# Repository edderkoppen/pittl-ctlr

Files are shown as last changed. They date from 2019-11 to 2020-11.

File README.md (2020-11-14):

# pittl-ctlr
Raspberry Pi TTL Controller, 0.2.0  
nGelwan | 2019

## Introduction
PiTTL is a collection of schematics and code which can be used to cheaply build a remotely-controllable random TTL sequence generator using a Raspberry Pi 4 (https://www.raspberrypi.org/products/raspberry-pi-4-model-b/) and a couple of additional hardware components. It consists of two parts, the PiTTL controller, contained in this repository, and the PiTTL client (https://github.com/extradosages/pittl-client). When pushed to the extreme, PiTTL supports generating sequences which run for at least a month consisting of pulses of less than 10ms duration. 

## Installation
### HAT Construction
If you don't have an already constructed PiTTL, one can be constructed relatively cheaply. The hardware for PiTTL has been designed like a Raspberry Pi HAT (https://www.raspberrypi.org/blog/introducing-raspberry-pi-hats/), to live on an auxiliary baord which talks to the Raspberry Pi via its GPIO headers. The schematics for the HAT are detailed in the **board** sub-repo (https://github.com/extradosages/pittl-ctlr/board), and can be viewed with EDA software. I used Eagle (https://www.autodesk.com/products/eagle/overview). The gerber files packaged in the **board** sub-repo can be supplied to a custom PCB-vendor in order to custom print the PCB for the HAT.

### Software Installation
One may install the PiTTL controller software on any Raspberry Pi, although the software has only been tested with the Raspberry Pi 4, and the practical limitation of the TTL driver listed above are given in the context of the hardware on a Raspberry Pi 4. Presumably, the software will function on a variety of operating systems, but certain features have been designed with Raspbian in mind (e.g. automatic start using systemd).

The only software prerequisites for the installation of pittld are python >=3.4, python setuptools, and a C-compiler for the compilation of pigpio. To setup and install the software, a very rudimentary shell script *setup/setup.sh* is provided, which should be run as root. Be warned, the setup script is non-transactional and doesn't try very hard to catch errors, so one should pay attention closely to stdout during the installation. If setup completes successfully, pittld may be started by entering

>*pittld*

at the command-line or-- assuming the installation of the systemd units succeeded-- automatically upon restart of the Raspberry Pi. The logs for pittld can be followed with  

>*journalctl -f -u pittld*

on Raspbian. Confirmation that pittld is running successfully can be found in journalctl or by observing updates on the HAT's LCD.

## Overview
### Usage
PiTTL can be used to stage and then generate individual sequences of TTL pulses, called **programs**. Generating-- also known as **staging**-- a program is a two-step process: first, the **timing** of the program is staged, and then the program's **sequence** is staged. If a sequence has been successfully staged, a program can be **started** and **stopped** at will.

**Timing** is specified with 3 parameters: the **total time**, **exposure fraction**, and **resolution**. Total time is the desired length of the program, exposure fraction is the desired fraction of the program during which TTL-on logic will occur, and resolution is the minimum width of a TTL-on pulse. The resolution parameter is *very* important. It drastically simplifies the algorithm for generating random sequences of pulses satisfying the desired exposure fraction. It is important to note that when these three parameters are supplied to PiTTL, that total time and exposure fraction will be adjusted so that the time spent in TTL-on and TTL-off are both integer multiples of the resolution, and so that they are as close to the values specified as possible. Thus, after staging, timing is converted into the **specified**, **adjusted**, and **digital** domains. The specified timing consists of those floating point values requested, adjusted are those values after adjustment for resolution, and digital are those values in integral units of resolution.

A **sequence** is literally a binary sequence representing the TTL-logic time-series of the program. PiTTL can be induced to randomly generate a sequence based on any valid staged timing. If a sequence has been staged and new timing is then staged, the two are then unrelated, and the staged sequence is purged.

Once a program has been **started**, the timing and the sequence are considered **committed**. New sequences and timing can be staged without interrupting the running program.

PiTTL is capable of evaluating the **progress** and **ETA** of a currently running program, and also **stopping** a program, clearing any committed timings and sequences.

This functionality is implemented via PiTTL controller's python API and publicly via the combination of the PiTTL controller's manager service and the PiTTL client (https://github.com/extradosages/pittl-client).

### Details
The PiTTL controller is organised into several related hardware components and software services. These are the:
1. Manager
2. TTL Driver
3. LCD
4. Connectivity monitor

The software services are packaged under the name **pittld**, for PiTTL Daemon.
#### The Manager
The manager provides a public endpoint for communicating with a PiTTL controller. It is the means by which a PiTTL client can command a PiTTL controller to stage timing and sequences and to start and stop programs, and also the means by which a PiTTL client can query a PiTTL controller for any staged or committed timing or sequences, or the progress of any running program.
#### The TTL Driver
This software service leverages the use of the python library PiGPIO (http://abyz.me.uk/rpi/pigpio/) and a MOSFET to generate the ~4.4V square wave pulses consituting a TTL pulse train.

This software includes the routines to approximately sample from the collection of all subsets of the unit interval with fixed measure without measure-zero components. A resolution parameter (defining the minimum width of a sampled pulse) specifies the accuracy (and memory burden) of the sampling routine, with asymptotic convergence to the ideal sampler upon decreasing the parameter. Once sampled, such a subset defines a pulse train via a mapping of the unit interval onto some interval (probably larger) interval of the time axis. Non-exhaustive testing has determined that *time \* resolution* reaches a practical minimum at ~10^-3 s^2 due to GPIO consdierations and that *time / resolution* reaches a practical maximum at ~0.2 \* 10\^9 due to memory considerations.

This software also contains routines to generate TTL-pulse trains of (ideally) arbitrary frequencey and duty-cycle, but as of 0.2.0 these have not been extensively tested.
#### The LCD
The PiTTL HAT was designed with a HD44780 16colx2row LCD which can convey information about connectivity and program progress without having to use the python API, pittld logs, or PiTTL client.
#### The Connectivity Monitor
The connectivity monitor supplies pittld with information regarding internet connectivity.

## Troubleshooting
If the PiTTL controller is not behaving as expected (usually indicated by oddities displayed on the HAT's LCD), or has encountered an error, the most robust way to fix the problem is to cycle the power on the Raspberry Pi. There has not yet been implemented a robust software means of resetting the pittld service.

Failure of the LCD on the PiTTL HAT should not a be a surprise. The HD44780 is cheap.

It is recommended that the PiTTL controller be installed on a dedicated Raspberry Pi, with a fresh OS. However, if it not the case, it is worth noting that
1. The PiTTL manager service needs to be able to listen on port 5000 in order to receive communications from a PiTTL client.

If problems persist, the software repository should be updated and the service reinstalled. If further problems persist, a fresh Raspbian should be installed.

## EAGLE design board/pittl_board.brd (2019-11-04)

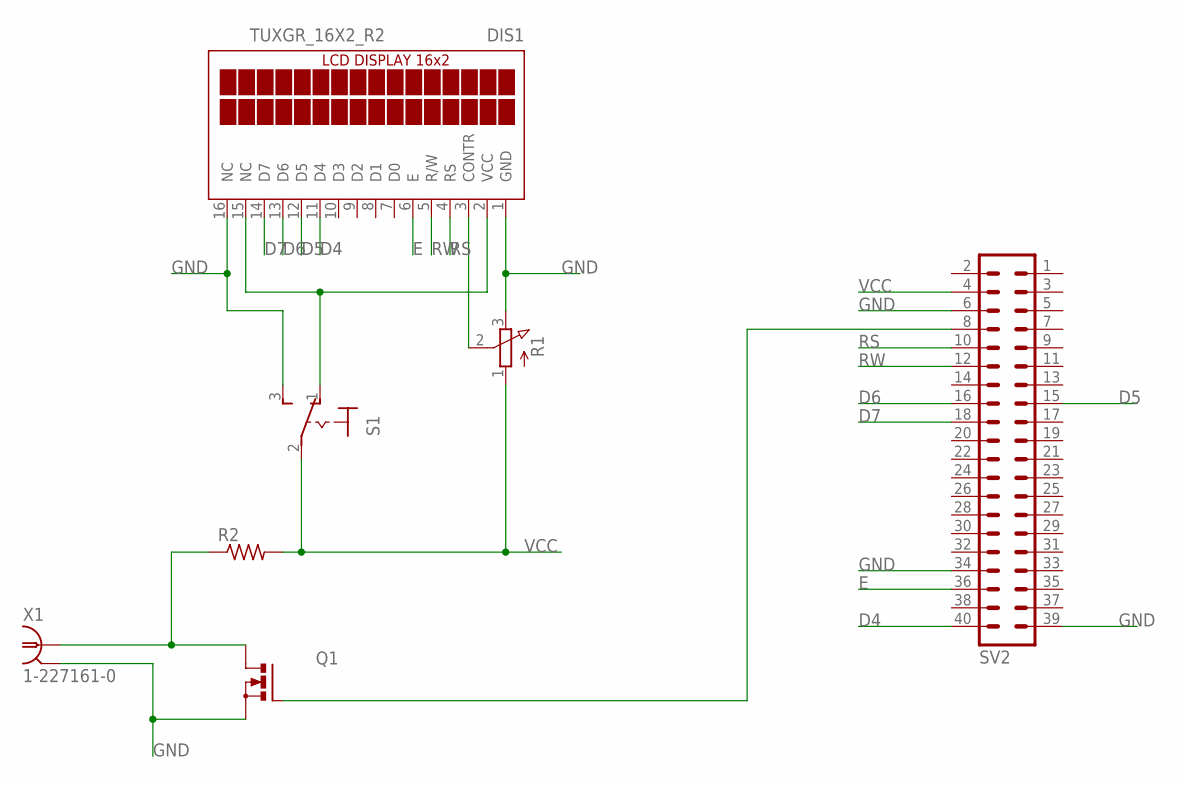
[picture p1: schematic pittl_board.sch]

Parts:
DIS1: TUXGR_16X2_R2
Q1: PMOSFET_NTO220BV; TO220BV
R1: 3RP/1610N
R2: R-US_0207/7; 0207/7
S1: 320-916
SV2: MA20-2W
X1: 1-227161-0; AMP_227161

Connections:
D4: DIS1.11 (D4), SV2.40
D5: DIS1.12 (D5), SV2.15
D6: DIS1.13 (D6), SV2.16
D7: DIS1.14 (D7), SV2.18
E: DIS1.6 (E), SV2.36
GND: DIS1.1 (GND), DIS1.16 (NC), Q1.S, R1.3 (E), S1.3 (S), SV2.6, SV2.34, SV2.39, X1.2
unnamed: Q1.G, SV2.8
unnamed: DIS1.2 (VCC), DIS1.15 (NC), S1.1 (O)
unnamed: DIS1.3 (CONTR), R1.2 (S)
unnamed: Q1.D, R2.1, X1.1
RS: DIS1.4 (RS), SV2.10
RW: DIS1.5 (R/W), SV2.12
VCC: R1.1 (A), R2.2, S1.2, SV2.4

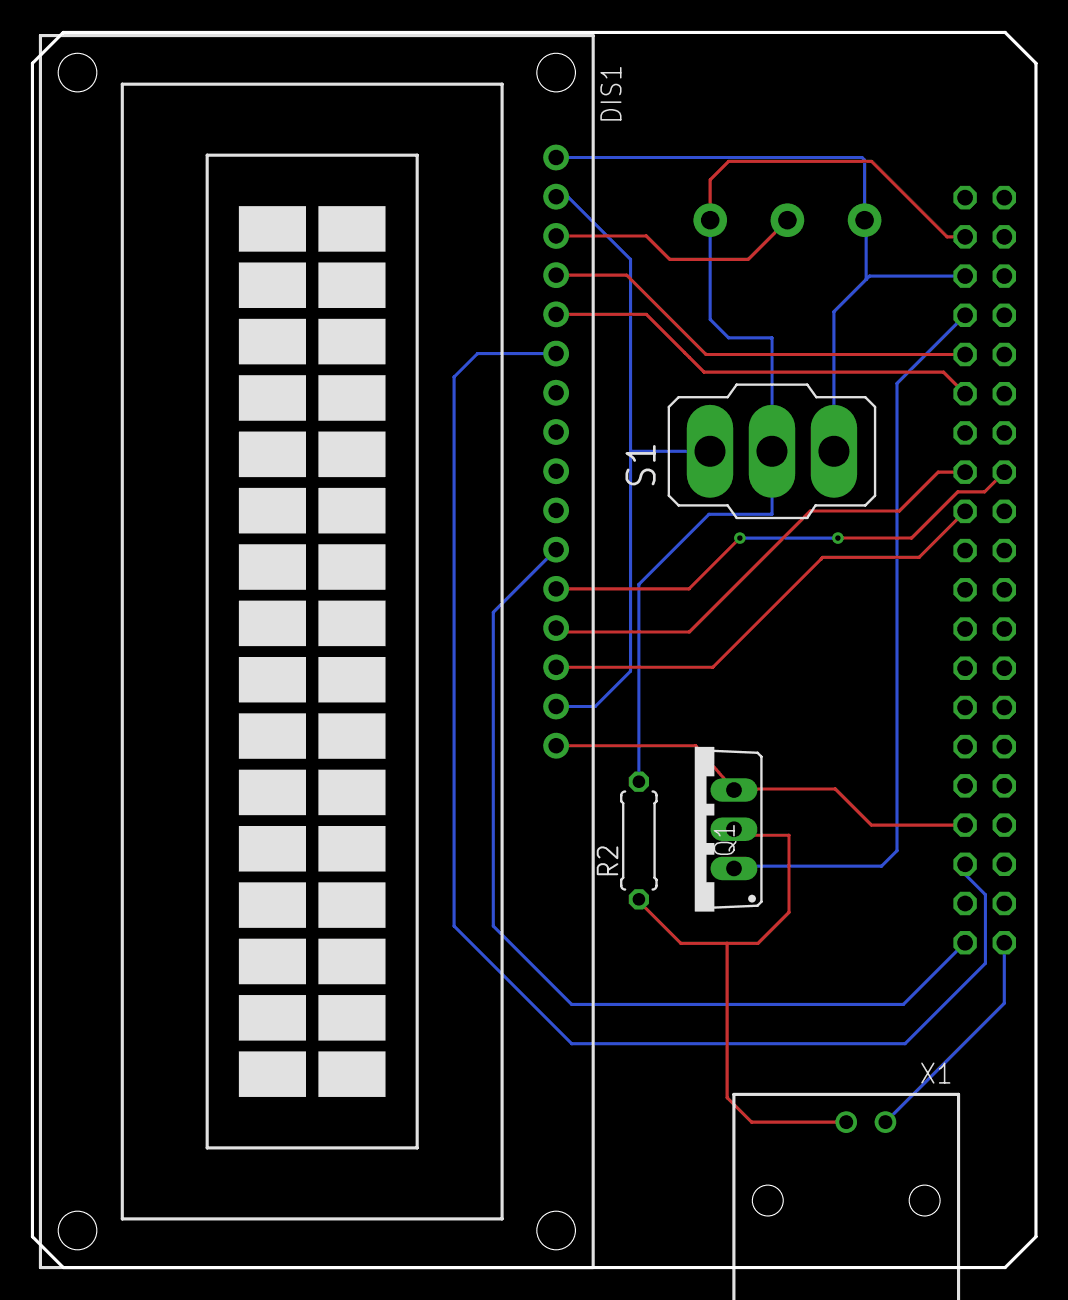
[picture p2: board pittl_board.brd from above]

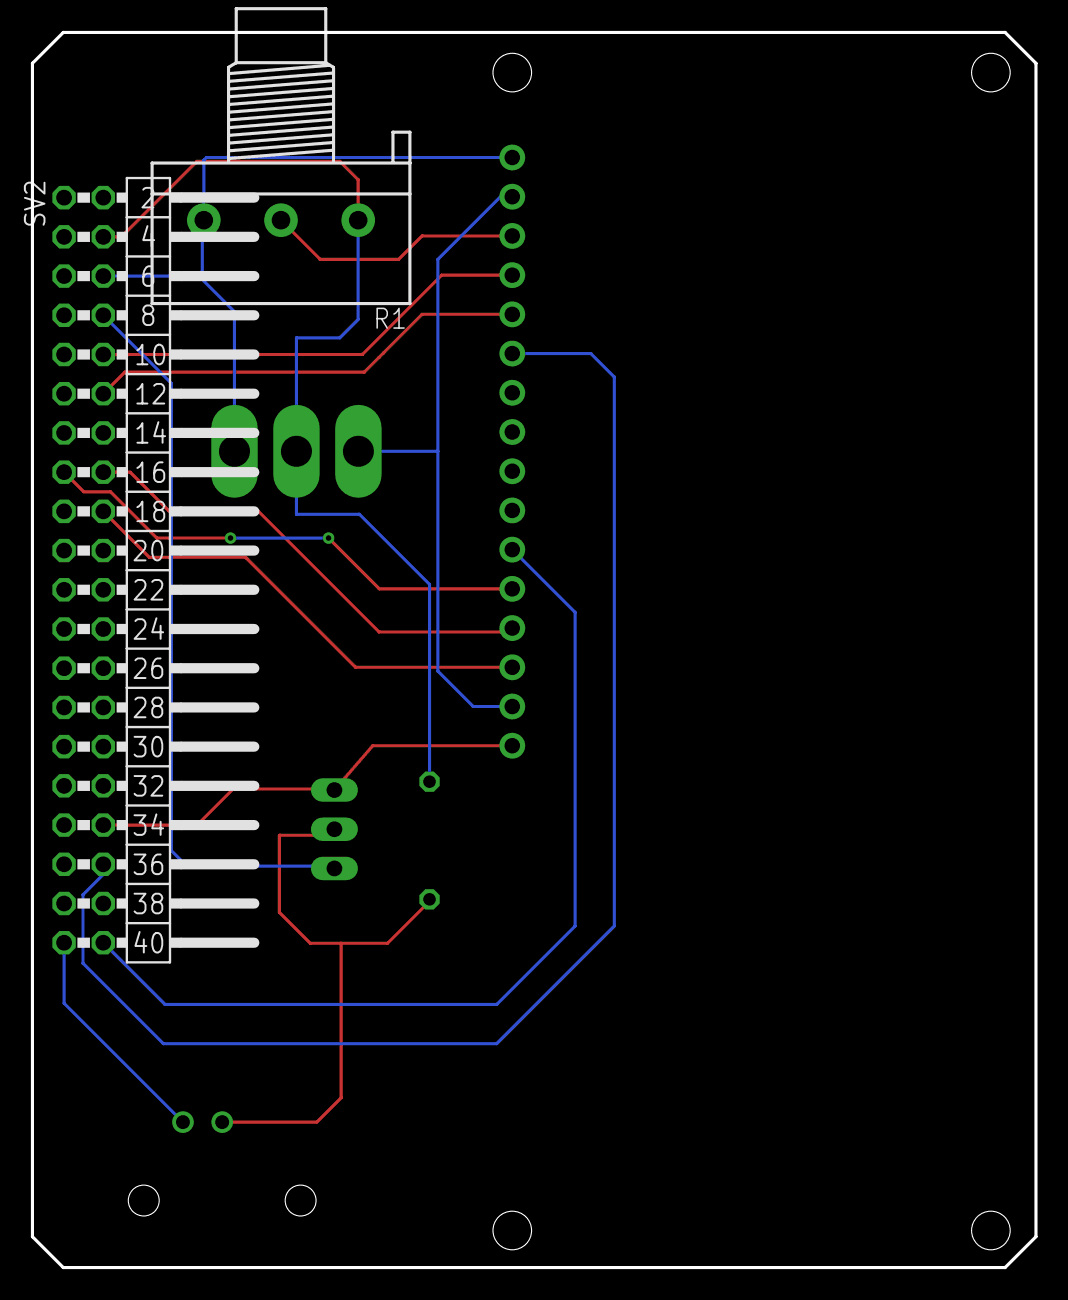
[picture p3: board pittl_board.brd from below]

Board: 2 copper layers, 65.0 x 80.0 mm, 7 parts (2 on the bottom side), 13 nets.

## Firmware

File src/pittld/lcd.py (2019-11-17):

from collections import namedtuple
from enum import Enum
import time
import queue

import pigpio
from RPLCD.pigpio import CharLCD

from pittld import logger
from pittld.svc import BaseService


# Constants
DELAY = 5


# Initialize lcd
pi = pigpio.pi()


# Service
class Service(BaseService):

    def __init__(self):
        super().__init__()
        self.name = 'lcd'

        self._lcd = CharLCD(pi,
                           pin_rs=15,
                           pin_rw=18,
                           pin_e=16,
                           pins_data=[21, 22, 23, 24],
                           pin_contrast=17,
                           cols=16, rows=2)

        self._row = [queue.Queue(), queue.Queue()]
        self._buffer = [[''], ['']]
        self._idx = [0, 0]

        self.reset()

    def run(self):
        logger.info('Starting lcd driver service')

        t0 = time.time()
        while True:
            for i in 0, 1:
                try:
                    buffer = self._row[i].get_nowait()
                    logger.debug('Retrieved new buffer {} in row {}'.format(buffer, i))
                    self._buffer[i] = buffer
                    self._idx[i] = 0
                except queue.Empty:
                    pass

            t1 = time.time()
            if t1 - t0 > DELAY:
                t0 = t1
                self.reset()
                time.sleep(0.2)
                self._update_display()

    def _update_display(self):
        line1 = self._buffer[0][self._idx[0]].ljust(16)
        line2 = self._buffer[1][self._idx[1]].ljust(16)

        self.reset()
        time.sleep(0.5)
        self._lcd.write_string(line1)
        time.sleep(0.5)
        self._lcd.crlf()
        time.sleep(0.5)
        self._lcd.write_string(line2)

        self._idx[0] = (self._idx[0] + 1) % len(self._buffer[0])
        self._idx[1] = (self._idx[1] + 1) % len(self._buffer[1])

    def put(self, row, buffer):
        try:
            self._row[row].get_nowait()
        except queue.Empty:
            pass
        self._row[row].put_nowait(buffer)

    def reset(self):
        self._lcd.cursor_mode = 'hide'
        self._lcd.clear()
        self._lcd.home()
